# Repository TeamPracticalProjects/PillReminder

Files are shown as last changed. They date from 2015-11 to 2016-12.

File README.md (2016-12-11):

# PillReminder
##A collaborative project by [Team Practical Projects](https://github.com/TeamPracticalProjects)

##What is the Pill Reminder?

As a person ages, we all know, it becomes more difficult to remember to take your pills. At some point a person is capable of living independently, but may not remember the current day of the week, or even what time of day. This can lead to a person taking more pills than they should, or to skipping a set of pills. The Pill Reminder is meant to be used by a person in this situation.

The assembled Pill Reminder project has 14 pill cups; one for AM and one for PM, all seven days of the week. Each pill cup has an LED associated with it. The LEDs are controlled by an Arduino processor. Only one LED is ever lit at a time. The Arduino keeps track of date and time so that the correct LED is on between 6am and noon, and another between 6pm and midnight. Our hope is that the user can be easily trained to only take pills when one of the LEDs is lit up. The LED that is on will tell them which pill cup to empty; if that cup is already empty, then they should not take more pills.

The care giver is responsible for assuring the correct operation of the Pill Reminder and for loading the pill cups as appropriate.

##How do you buy a Pill Reminder?

You can't buy one. The Pill Reminder is a do-it-yourself project. All the information you need to buy the parts and assemble you own Pill Reminder can be downloaded from this site - and it's free for non-commercial use!

##The History

The Pill Reminder is a project that came about through a conversation at a Baby Boomer Makers meet-up held at the Mid Peninsula TechShop (www.techshop.ws) one cold winter evening in 2013. Bob Glicksman had the idea for the Pill Reminder and said he always wanted to make one, but he could not find the right case. Jim Schrempp had been looking for a project and said, “if you make two of the electronics I'll make two of the cases.” That night the collaboration was born.

Bob and Jim agreed to make the project and release the plans as an open source project freely licensed for non-commercial use. As a user of these open source plans you make make one, or several, for you own use but you cannot make them to sell. If you modify the plans or kits in some way you are obligated to publish your modifications and to also license your modified plans under the same terms. Your modified plans must contain attribution back to Bob Glicksman and Jim Schrempp.

Since we built this project, there have been a number of sophisticated smart phone apps released to help with medication compliance. They are not suitable for someone who doesn't actively use a smart phone. Some of them have surprisingly good features. Jim did some research and wrote an article on the criteria he used and ends with a recommendation of [the best pill reminder app](https://www.techenhancedlife.com/citizen-research/best-pill-reminder-app-explorer-choice).

We hope you enjoy the project!  
Jim Schrempp and Bob Glicksman  
San Francisco Bay Area  
February 2014

Here's a [video of an early version](https://www.youtube.com/watch?v=8NOZzQJS1Nk) of the Pill Reminder.

Tags: pill reminder, drug reminder, prescription reminder, free, open source

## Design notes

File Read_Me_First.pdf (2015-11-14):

Pill Reminder – release 1.0

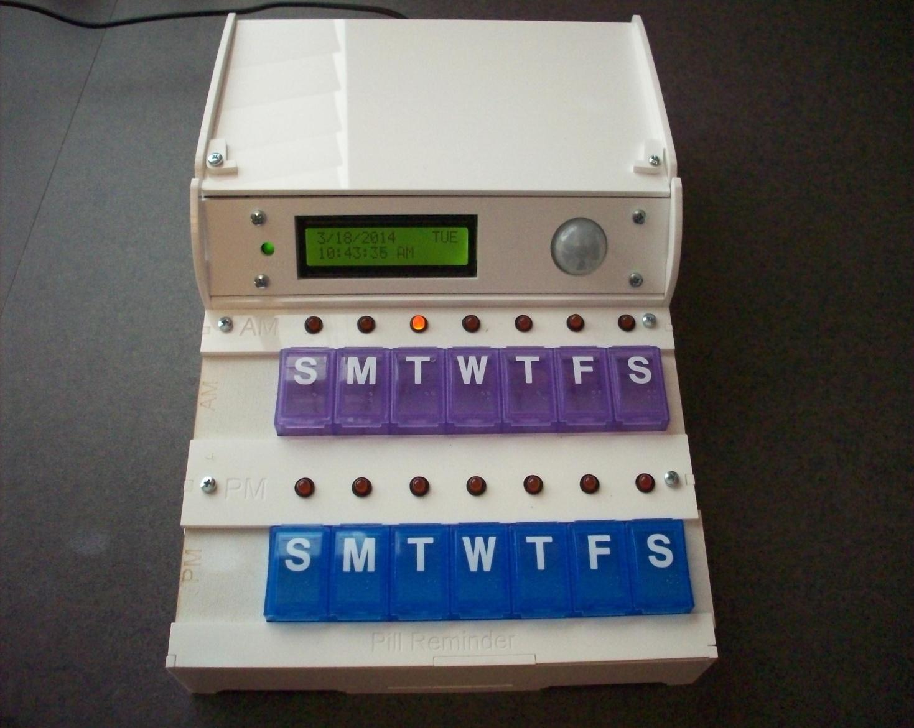
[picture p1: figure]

© 2014 Shrimpware LLC. All rights reserved.

# Pill Reminder

# Introduction and Overview of the version 1.0 Release Package

### Shrimpware LLC

5/14/2014

### Read this document first!

© 2014 Shrimpware LLC | Page 2

## License and Disclaimer

The Pill Reminder is subject to the terms of use, licenses and disclaimers contained in the document “Terms_Of_Use_License_and_Disclaimer” that is included with this release package. This document can also be viewed at: http://www.shrimpware.com/pillreminder/TOU.html

Copyright © 2014 Shrimpware LLC. All rights reserved.

The material contained within this release package may not be copied, duplicated, or reproduced in whole or in part using any method, for any reason, or under any circumstances without expressed written permission by Shrimpware LLC. Individuals may download and keep one unaltered copy for non-profit, personal use of the contents.

© 2014 Shrimpware LLC | Page 3

## Table of Contents

### Contents

1 | Introduction | 4
2 | Contents of the Release Package | 5
3 | Pathways | 7
3.1 | Pathway #1: Building and Using the Pill Reminder | 7
3.2 | Pathway #2: Manufacturing Your Own Enclosure Parts or Modifying the Enclosure
Design | 7

3.3 Pathway #3: Fabricating your own Shield Board or modifying the Shield Board design. 8

3.4 | Pathway #4: Modifying the Pill Reminder Software | 8
4 | History | 10
5 | Frequently Asked Questions (FAQ) | 12
5.1 | How can I buy a Pill Reminder that is already assembled and tested? I do not wish to
purchase piece parts and build one | 12

5.2 Where can I purchase a complete set of parts for the Pill Reminder, so that I do not have
to buy parts from the many vendors in the Parts List? | 12
5.3 | How do I use and maintain the Pill Reminder once I have built and tested it? | 12
5.4 | The default pill taking times do not address my needs. How can I change these? ....... 12
5.5 | The timekeeping function of the Pill Reminder is US specific. I live in a different
country that observes “summertime” whose dates and time changes differ from US daylight
savings time. How can I modify the Pill Reminder to observe my summertime rules? | 13

5.6 I like the Pill Reminder concept, but the plans in this package are for a device that supports only morning and evening pills. I need a Pill Reminder that supports three or four
pill taking periods per day. How can I obtain a Pill Reminder that meets my needs? | 14

© 2014 Shrimpware LLC | Page 4

1 Introduction.

The Pill Reminder is a very simple to use device to remind someone to take their medications (pills). This version of the Pill Reminder supports morning and evening pill sets.

The Pill Reminder is intended to provide the User with a very simple, even intuitive, means to determine what medications may be taken at any given time and day. In this regard, the Pill Reminder differs from many other devices that are intended to alert, even nag, the User to take their pills. The Pill Reminder shows the User what medications may be taken at any given time and, by exception, what medications should not be taken at that time. The difference here is subtle, but important. The Pill Reminder is intended as an aid not only to help Users avoid missing taking their pills (under medicating), but equally to help Users avoid taking duplicate sets of pill or sets of pills spaced too closely in time (over medicating).

The Pill Reminder is released by Shrimpware LLC as an open source, do it yourself (DIY) project. This release package contains complete material to allow you to procure parts, build your Pill Reminder, operate your Pill Reminder, and possibly even modify your Pill Reminder. You must assemble the Pill Reminder yourself based upon the documentation contained in this release package. Shrimpware LLC is not a manufacturer, supplier or distributor of the Pill Reminder, nor of any of its component parts, nor of the documentation in this release package. Shrimpware LLC is only acting as a repository from which you may download this release package and the documentation contained herein.

The material in this release package is subject to terms of use, license and disclaimers contained in the document “Terms_Of_Use_License_and_Disclaimer” that is included with this release package. This document can also be viewed at: http://www.shrimpware.com/pillreminder/TOU.html

You may use any material in this release package for your own personal and non-commercial use, according to the license described in the aforementioned “Terms_Of_Use_License_and_Disclaimer” document.

The material in this release package requires that you build the Pill Reminder yourself, using only the materials and documentation contained herein. Please review all materials and documents in this package prior to purchasing any parts or attempting any assembly. It is your responsibility to ensure that you have the skills, tools and means to complete and use the Pill Reminder safely, using only the materials contained herein. Shrimpware LLC cannot provide technical support and you are on your own if you run into problems or have trouble completing the Pill Reminder or making it work.

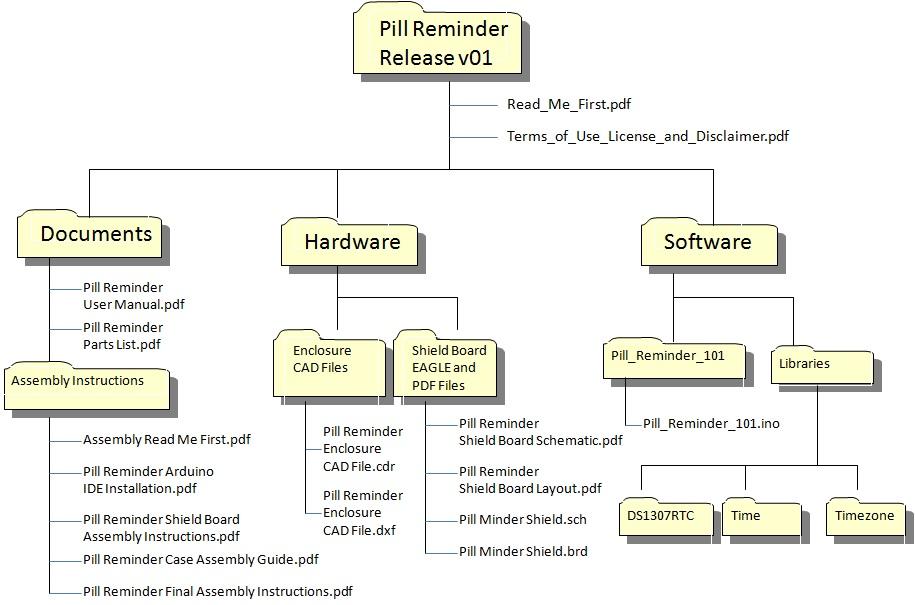
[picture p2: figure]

© 2014 Shrimpware LLC | Page 5

2 Contents of the Release Package.

The diagram below depicts the contents and organization of this release package. The release package is a .zip archive and you must download this archive to your computer and unzip it before you can access any of the material contained herein.

This release package is organized as a series of folders and subfolders, as shown in the figure above. A brief description of the package contents, by folder, is given below:

- Top Level Folder. The top level folder “Pill Reminder Release v01” contains this document and the document “Terms_Of_Use_License_and_Disclaimer”. You must read and agree to all of the terms and conditions in the latter document before you have permission to use any other material in this package.
- Documents. The “Documents” folder contains all of the documents that you will need to build and to operate the Pill Reminder. The folder contains the User Manual and Parts List. The subfolder “Assembly Instructions” contains a series of documents for assembling and testing the major subsystems of the Pill Reminder, as well as Final Assembly Instructions for integrating and testing the Pill Reminder. The document “Assembly Read Me First” will lead you though the rest of the documents in this subfolder.

© 2014 Shrimpware LLC | Page 6
- Hardware. This folder contains CAD files for both the enclosure and the shield board. You do not need these files to build and operate the Pill Reminder. They are provided as part of the open source concept so that you have complete information about the Pill Reminder, including files that you can use, subject to the open source license, to make your own modifications to the Pill Reminder.
- Software. This folder contains the software files that you must compile and upload to your Pill Reminder in order for it to operate. The Pill Reminder software, in the folder “Pill_Reminder_101” is source code that you can alter, subject to the open source license, to make your own modifications to the Pill Reminder. This software is written in the “wiring” language for the Arduino computer that is part of the Pill Reminder. You do not need to make any modifications to this software to build and operate the Pill Reminder, but you do need to compile it and upload it to your Arduino Uno microcontroller board, along with the libraries contained in the “Libraries” subfolder, in order for the Pill Reminder to operate. Complete instructions for installing the Arduino IDE on your computer, for adding the libraries in this package to your IDE, and for compiling and uploading the software to the Arduino Uno board that is part of the Pill Reminder, are contained in the document “Pill Reminder Arduino IDE Installation” that is included in
the “Documents | Assembly Instructions” folder.

© 2014 Shrimpware LLC | Page 7

3 Pathways.

The documentation that is included in this release package and described in section 2 above may be used in a number of application pathways. The pathways and the documents needed for each are described in this section.

3.1 Pathway #1: Building and Using the Pill Reminder.

The “Documents” folder contains all of the instructions that you need to build and operate the Pill Reminder. Under “Documents” you will find the User Manual and the Parts List. The Parts List contains a list of all parts (but not tools and materials) that you will need to buy in order to assemble one or more Pill Reminders. All parts can be ordered over the Internet using the links provided in the Parts List. It must be noted that certain links in the Parts List provide more parts than are needed for a single Pill Reminder; i.e. 3 shield boards (one is needed), 20 micro pushbutton switches (3 are needed), etc. This is an inevitable consequence of a small quantity build and you might want to find other Pill Reminder builders to consolidate a parts order for more cost effective parts procurement.

The “Assembly Instructions” subfolder contains a series of documents that describe, in annotated step by step detail, the assembly instructions for all parts of the Pill Reminder, and for the integration and testing of these parts into a finished unit. The “Assembly Read Me First” document provides a detailed overview. Each of the detailed assembly documents lists the tools and materials needed for that stage of the assembly.

You should read through all documents in the “Documents” folder first, before you order any parts, begin any assembly, or otherwise undertake any part of this project. It is your responsibility to ensure that you are prepared to undertake a project of this scope and magnitude.

### 3.2 Pathway #2: Manufacturing Your Own Enclosure Parts or Modifying the Enclosure

Design.

The folder “Hardware | Enclosure CAD Files” contains two versions of the 2D CAD drawings
for the parts needed to build the Pill Reminder enclosure. You do not need to use these files because the Parts List contains a link to a vendor that can supply these parts, pre-cut, for you. However, you may elect to fabricate these parts yourself, for which you will need these CAD files and a laser cutter.

There are two CAD files in this subfolder. The files are for the identical design and you only need one of them. The file “Pill Minder.cdr” is in Corel Draw’s internal file format, and the file “Pill Minder.dxf” is the same CAD file converted to this more common format. These CAD files are provided to you as-is. We have made our best effort to ensure accuracy and correctness of the data therein; however, if you use them, you are on your own!

© 2014 Shrimpware LLC | Page 8

You may also use these files to modify the enclosure in Coral Draw or using any other 2D CAD program that you can import either of these files into. Any modifications that you make are subject to the terms and conditions, license and disclaimers contained in the document “Terms_Of_Use_License_and_Disclaimer” that is included with this release package.

### 3.3 Pathway #3: Fabricating your own Shield Board or modifying the Shield Board

design.

The folder “Hardware | Shield Board EAGLE and PDF Files” contains the following
information:
- “Pill Reminder Shield Board Schematic.pdf” is a pdf version of the shield board schematic diagram. It is provided for those who wish to view, but not modify, the schematic.
- “Pill Reminder Shield Board Layout.pdf” is, likewise, a pdf version of the shield board printed circuit layout. It is provided for those who wish to view, but not modify, the board layout.
- The files “Pill Minder Shield.sch” and “Pill Minder Shield.brd” are EAGLE files produced by the EAGLE electronic CAD software from Cadsoft corporation (version 6.5.0). See www.cadsoft.de for further information or to download a free, hobbyist version of this software.

You do not need any of these files to build or use the Pill Reminder, as the blank shield board can be procured from a vendor listed on the Parts List. However, you may use the EAGLE CAD files to procure shield board PC boards from another vendor of your choice, to manufacture your own shield boards if you have printed circuit manufacturing capability, or to modify the shield board electronic design to tailor the Pill Reminder to your needs. Any modifications that you make are subject to the terms and conditions, license and disclaimers contained in the document “Terms_Of_Use_License_and_Disclaimer” that is included with this release package.

3.4 Pathway #4: Modifying the Pill Reminder Software.

The folder “Software | Pill_Reminder_101” contains the source code for the Pill Reminder. It is
provided to you subject to the terms and conditions, license and disclaimers contained in the document “Terms_Of_Use_License_and_Disclaimer” that is included with this release package.

The software is written in the “wiring” language, which is the standard programming language for the Arduino. The software has been written, compiled and tested under the Arduino IDE version 1.0.5. You do not have to make any modifications to this software, nor know anything about the wiring language or programming an Arduino, in order to build the Pill Reminder and use it as described in the User Manual. However, we have attempted to extensively comment the

© 2014 Shrimpware LLC | Page 9

source code so that you can understand it, if you wish, and make modifications to it as you see fit. Any modifications that you make to the Pill Reminder software is your own responsibility and Shrimpware LLC cannot provide and consultation or technical support regarding the released software or any modification(s) that you make therein.

See section 5, FAQ, for a discussion of some specific changes that you might wish to make in the Pill Reminder software in order to further customize it to meet some specific needs.

© 2014 Shrimpware LLC | Page 10

4 History.

The Pill Reminder is a project that came about through a conversation at a “Baby Boomer Makers, Hackers, and Entrepreneurs” meet-up held at the Mid Peninsula TechShop (www.techshop.ws) one cold January evening in 2014. Bob Glicksman had the idea for the Pill Reminder and said he had wanted to make one for a long time, but he could not find the right case. Jim Schrempp had been looking for a project and said: “if you design the electronics, I will design the enclosure.” That night, the collaboration was born.

Bob was inspired to invent the Pill Reminder out of need to support his elderly mother (“Mom”). Mom has dementia and near total short term memory loss. Bob had long supplied her with her medications in weekly “AM/PM” pill organizers. Bob would call Mom twice a day, morning and evening, to remind her to take her medications. Nevertheless, at the weekly refill time, Bob would frequently find either that Mom had missed taking some pills, or alternatively (perhaps worse), Mom would call a day or two before the pills should have run out to say that she was out of pills (meaning that she took multiple day doses, possibly leading to overdosing).

Bob experimented with many products and means to help Mom prevent overdosing; for example, mounting a clock over bathroom sink with the day of the week displayed in large letters. Nevertheless, the compliance issues persisted. Bob came up with the basic Pill Reminder concept after being frustrated with failure after failure of existing products to solve the problem. Bob reasoned that the issue with Mom was a failure to comprehend when to take what medicines and when not to take some medicines. Bob thought that a simple and intuitive method of signaling Mom when she could open a pill dispenser slot (and take any pills therein), and when she should not open a slot, would be the key to solving the problem.

The “Baby Boomer Makers, Hackers, and Entrepreneurs” meet-up group was of great assistance in flushing out the device requirements, present and potential future features, and in finalizing a development specification. Jim and Bob then went off to design, develop, test and document the Pill Reminder.

As of the date of this writing, Mom has had her Pill Reminder for over 4 weeks and has achieved 100% compliance throughout. Previously, Mom would have a fully compliant week only once in every three, on the average. Four weeks in a row of perfect compliance is highly significant, even given that it is early in deployment and testing.

The only instructions given to Mom were: “if a light is lit, open the dispenser slot under the light and take any pills in it. If there are no pills in it, then you have already taken them, even if you don’t remember doing so. Under no circumstances are you to open a dispenser slot when the light above it is not lit”. In follow up research, Mom has been unable to articulate the meaning of the light over each pill slot. Clearly, then, these excellent early results demonstrate that Pill Reminder operation is quite intuitive (a major goal when dealing with people with short term memory loss).

To date, Bob and Jim have constructed three additional Pill Reminders from the plans and instructions released in this package. Although these three devices have not yet been deployed to people who really need them, they are all running and proving (a) that the build instructions

© 2014 Shrimpware LLC | Page 11

seem to be clear and complete, and (b) that the Pill Reminders operate reliably in a “real world” environment.

Bob and Jim agreed early on to release the Pill Reminder plans as an open source, do it yourself (DIY) project, freely licensed for non-commercial use. By including all source code and source CAD files, they hope that people will not only make Pill Reminders for their own use or as gifts, but will customize and modify the design and openly and freely share their efforts with the user community. For example, you can use the 2D mechanical CAD files to make your own enclosure. The enclosure can be cut from 3mm Baltic birch plywood for “cheap but cheerful” version, and spray painted however you like. Alternatively, the pieces can be cut out of your favorite color 3mm (0.118 inch) acrylic for the more “real product” look. If you are so inclined, you might want to use a 2D CAD program to modify the design of the enclosure to create a different look, or to better fit onto a bathroom sink or night stand. We would be very interested in other people’s ideas for improvement. Please e-mail your thoughts, ideas, experiences, and modifications to pillreminder@shrimpware.com.

© 2014 Shrimpware LLC | Page 12

5 Frequently Asked Questions (FAQ).

This section contains some frequently asked questions and their answers.

### 5.1 How can I buy a Pill Reminder that is already assembled and tested? I do not wish to

purchase piece parts and build one.

As of this writing, the Pill Reminder is only available as an open source, do it yourself (DIY) project, based upon the material in this release package. Nobody is presently licensed to manufacture or sell fully or partially assembled Pill Reminders. If you are interested in manufacturing or selling fully or partially assembled Pill Reminders, please contact us at: pillreminder@shrimpware.com

### 5.2 Where can I purchase a complete set of parts for the Pill Reminder, so that I do not

have to buy parts from the many vendors in the Parts List?

As of this writing, the Pill Reminder is only available as an open source, do it yourself (DIY) project, based upon the material in this release package. Nobody is presently licensed to manufacture or sell parts kits or partially assembled Pill Reminders. If you are interested in manufacturing or selling parts kits or partially assembled Pill Reminders, please contact us at: pillreminder@shrimpware.com

### 5.3 How do I use and maintain the Pill Reminder once I have built and tested it?

Please see the User Manual for complete information about operating and maintaining your Pill Reminder. The “Pill Reminder User Manual” can be found in the “Documents” folder of this release package.

### 5.4 The default pill taking times do not address my needs. How can I change these?

The Pill Reminder software uses generic times for allowable taking of AM and PM pills. These times are specified by defined constants in the Pill Reminder software. Since you have the source code available, you may change these defined constants to fit your needs.

When you open the Pill Reminder software in the Arduino IDE, you can read more about these defined constants in the comments at the top of the program (lines 11 through 20). You can change the defined constants that control these times by editing lines 159 through 162 of the software. You must then recompile and upload the software to your Pill Reminder (Arduino Uno board) in order for the new times to take effect.

Please note that the software design requires that you leave at least one minute between AM off time and PM on time, and likewise between PM off time and AM on time. If you do not do so, the proximity sensor will not re-arm and the LEDs will not blink when the proximity sensor is tripped the first time during any pill taking period.

© 2014 Shrimpware LLC | Page 13

You are fully responsible for any and all changes that you make to the Pill Reminder software. If you do make changes to the software, please make sure to test your revised software completely and thoroughly before releasing the altered Pill Reminder for use. Please note that you are required, under our licensing agreement, to release your modifications as open source, non-commercial and provide proper attribution to us.

### 5.5 The timekeeping function of the Pill Reminder is US specific. I live in a different

country that observes “summertime” whose dates and time changes differ from US daylight savings time. How can I modify the Pill Reminder to observe my summertime rules?

The Pill Reminder software uses a “Timezone” library written by Jack Christensen and downloaded from https://github.com/JChristensen/Timezone.

Lines 187 and 188 of the Pill Reminder software define structures that are used by this library to implement changes from standard time to daylight savings time and again from daylight savings time back to standard time. The two lines of code are:

- TimeChangeRule dt = {"DT", Second, Sun, Mar, 2, 60};
- TimeChangeRule st = {"ST", First, Sun, Nov, 2, 0};

You can read about these structures, and how to change them, in the documentation for the Timezone library at the url given above. Specifically, the second and third arguments specify which day of which month (4th argument) the change is to take place, and the last argument specifies the magnitude of the change in minutes. Consequently, the change “DT” (first argument) is to take effect beginning on the Second, Sunday (Sun), at 2 AM, and it is to add 60 minutes to the “normal” time. Likewise, the change “ST” (first argument) is to take effect beginning on the First, Sunday (Sun), at 2 AM, and it is to add zero minutes to the “normal” time.

Please note that the Pill Reminder software does not use the Timezone library to convert to and from UTC, as the library’s author intends. It only uses the Timezone library to implement a one hour (60 minute) shift from the standard to daylight savings time, according to the dates and times defined in these structures.

Since you have the Pill Reminder source code, you can open it in the Arduino IDE and make any changes that you wish. You can change these structures to change the dates and time of day that the changes to and from summertime take place in your locale, as well as the magnitude of the change (in minutes). You must then recompile and upload the software to your Pill Reminder (Arduino Uno board) in order for the new daylight savings time definitions to take effect.

© 2014 Shrimpware LLC | Page 14

You are fully responsible for any and all changes that you make to the Pill Reminder software. If you do make changes to the software, please make sure to test your revised software completely and thoroughly before releasing the altered Pill Reminder for use. Please note that you are required, under our licensing agreement, to release your modifications as open source, non-commercial and provide proper attribution to us.

### 5.6 I like the Pill Reminder concept, but the plans in this package are for a device that

supports only morning and evening pills. I need a Pill Reminder that supports three or four pill taking periods per day. How can I obtain a Pill Reminder that meets my needs?

This release of the Pill Reminder only supports AM and PM pills. Extensive changes would need to be made in order to support more pill taking times. These changes include:

- Re-design of the enclosure to hold more pill dispensers and house more LEDs.
- Re-design of the shield board to extend the shift register that drives the LEDs and to add connectors for the extra LEDs.
- Extensive changes to the software in order to accommodate more LEDs and act upon more pill taking intervals.

This release package contains all of the source files (mechanical CAD, electrical CAD, and software source) for the Pill Reminder and it is therefore possible to use this material to re-design the Pill Reminder for more pill taking times. The scope of this effort is large, however, and you should only attempt it if you have the necessary skills in mechanical design, electrical design and Arduino software development that are all needed to make such an extensive re-design work. If you do accomplish this, please follow the license requirements and release your modifications as open source, non-commercial, with proper attribution to us. And please let us know that you did this by e-mailing to: pillreminder@shrimpware.com

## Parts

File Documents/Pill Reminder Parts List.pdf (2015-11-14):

Shrimpware LLC | PILL REMINDER | Parts List
Assembly | Item | Qty | Part Number | Source | Description | On-Line Purchase Link | Unit Price | Ext Price | Notes
Enclosure
Parts kit | 1 | 1 | N/A | Make it yourself or order from Prawn Designs | Kit of parts for assembling the enclosure | http://www.prawndesigns.com | | $30.00 | The enclosure parts can be fabricated using the CAD files an Assembly instructions in this release package.
; info@prawndesigns.com
Pill Dispenser | 2 | 4 | Weekly Pill Planner with Snap-Tight Lids, CVS p/n
| | | 715123
CVS Pharmacy | Removable plastic weeekly pill
dispenser

http://www.cvs.com/shop/product-detail/CVS-Large-Weekly-Pill-Planner?skuId=715123 (http://www.cvs.com/shop/product-detail/CVS-Large-Weekly-Pill-Planner?skuId=715123)

$2.99 | $11.96 | Best to get two colors, e.g. 2 ea
clear for AM and 2 ea Blue for PM
LED - yellow | 3 | 7 | LED panel mount, amber; PN 607-5102H3-5V
Mouser | Panel mount amber LED with
internal resistor and 6" pigtail leads ("AM" day indicators)

http://www.mouser.com/ProductDetail/Chicago-Miniature/5102H3- (http://www.mouser.com/ProductDetail/Chicago-Miniature/5102H3-5V/)

$1.30 | $9.10 | LED with internal resisotor; Amber
for AM LEDs
LED- green | 4 | 8 | LED panel mount, green; PN 607-5102H5-5V
Mouser | Panel mount green LED with
internal resistor and 6" pigtail leads ("PM" day indicators and power on http://www.mouser.com/Prod (http://www.mouser.com/ProductDetail/Chicago-Miniature/5102H3-5V/) uctDetail/Chicago-Miniature/5102H5- (http://www.mouser.com/ProductDetail/Chicago-Miniature/5102H5-5V/)
$1.30 | $10.40 | LED with internal resisotor; Green
for PM and Power LEDs
Display | 5 | 1 | LCD display, 16x2, backlit; ID: 181
Adafruit | 16x2 character LCD display, backlit,
HD44780 controller

http://www.adafruit.com/prod (http://www.mouser.com/ProductDetail/Chicago-Miniature/5102H5-5V/) ucts/181 (http://www.adafruit.com/products/181)

$9.95 | $9.95 | Can get two for 4.98 here:
http://www.ebay.com/itm/2pcs-1602-16x2-Character-LCD-Display-Module-HD44780-Controller-yellowblacklight-
/400446382818?ssPageName=ADM E:X:RTQ:US:1123
Proximity Sensor | 6 | 1 | 5V PIR module, 3.3V output; ID: 189
Adafruit | Passive infra-red proximity sensor,
with 3 pin cable

http://www.adafruit.com/products/189 (http://www.adafruit.com/products/189)

$9.95 | $9.95
Real-time clock | 7 | 1 | High accuracy "Chronodot" RTC I2C Module; ID: 255
Adafruit | Real-time, battery backed, clock
module, DS3231 based, I2C
interface

http://www.adafruit.com/products/255 (http://www.adafruit.com/products/255)

$17.50 | $17.50 | Compatible for DS1702 based RTC
modules, but this model uses temp[erature compensated internal crystal for high accuracy and stability.
Microcontroller | 8 | 1 | Arduino Uno R3 board; Mouser P/N 782-A000066
Mouser | Arduino Uno Rev 3 microcontroller
board.

http://www.mouser.com/ProductDetail/Arduino/A000066/?qs=sGAEpiMZZMtE4ePzUE8d2Ju
FIVM5Ac0l (http://www.mouser.com/ProductDetail/Arduino/A000066/?qs=sGAEpiMZZMtE4ePzUE8d2JuFIVM5Ac0l)
$24.51 | $24.51 | Also available from Adafruit:
http://www.adafruit.com/products/50
Cable, separable | 9 | 1 | 40 wire, female pin header cable, separable; ID: 266
Adafruit | Separable 0.1" pin header female-
female cables.

http://www.adafruit.com/products/266 (http://www.adafruit.com/products/266)

$6.95 | $6.95 | Many alternate sources available.
Power Adaptor | 10 | 1 | 9 volt DC wall wart power supply; Mean Well P/N GS06U-2P1J
Jameco | 9 volt, 660 ma, DC "wall wart"
power adapter, for Arduino http://www.jameco.com/webapp/wcs/stores/servlet/Product_10001_10001_1940686_-1 (http://www.jameco.com/webapp/wcs/stores/servlet/Product_10001_10001_1940686_-1)
$9.49 | $9.49
USB Cable | 11 | 1 | USB A/B cable; ID: 62 | Adafruit | USB cable for programming the Arduino Uno

http://www.adafruit.com/products/62 (http://www.adafruit.com/products/62)

$4.00 | $4.00
Pin header | 12 | 1 | 10 pcs 1x36 breakable male pin header; ID: 392 | Adafruit | Breakable, male, PB board solderable, 0.1" pin headers

http://www.adafruit.com/products/392 (http://www.adafruit.com/products/392)

$4.95 | $4.95
Mounting Hardware | 13 | 14 | metal screw, 4 - 40; p/n 534-9901
Mouser | Flat head 4 - 40 metal screw, 3/8"
long

http://www.mouser.com/ProductDetail/Keystone-Electronics/9901/?qs=sGAEpi MZZMtFmYSM%2fWUJwjMM2
jkmYE8TyGoG3vEKdJ8%3d (http://www.mouser.com/ProductDetail/Keystone-Electronics/9901/)
$0.10 | $1.40
Mounting Hardware | 14 | 4 | metal standoff, 4 - 40; p/n 761-2112-440-AL-7
Mouser | Double sided, 4 - 40 metal
standoff, 1" high

http://www.mouser.com/ProductDetail/RAF-Electronic-Hardware/2112-440-AL-7/?qs=sGAEpiMZZMtrde5aJd3
qw8BUoqM2q3%252bQgGcuZ
%252bZQnXw%3d (http://www.mouser.com/ProductDetail/RAF-Electronic-Hardware/2112-440-AL-7/)
$0.40 | $1.60
pp 1 of 3 | 5/22/14 | Copyright (c) Shrimpware LLC. All rights reserved.

Mounting Hardware | 15 | 10 | metal nut, 4 - 40; p/n 534- 7235-3
Mouser | 4 - 40 metal hex nut | http://www.mouser.com/Prod
uctDetail/Keystone-Electronics/7235-
3/?qs=sGAEpiMZZMtFmYSM%
2fWUJwjMM2jkmYE8TVaKr94Y
YEsQ%3d (http://www.mouser.com/ProductDetail/Keystone-Electronics/7235-3/)
$0.06 | $0.60
Mounting Hardware | 16 | 7 | nylon screw, 4 - 40; p/n 534-9328
Mouser | flat head nylon screw, 4 - 40, 3/8"
long

http://www.mouser.com/ProductDetail/Keystone-Electronics/9328/?qs=sGAEpi MZZMtFmYSM%2fWUJwjMM2
jkmYE8TDv833dWoJEQ%3d (http://www.mouser.com/ProductDetail/Keystone-Electronics/9328/)
$0.13 | $0.91
Mounting Hardware | 17 | 2 | nylon screw, 4 - 40; p/n 534-9527
Mouser | flat head nylon screw, 4 - 40, 1/4"
long

http://www.mouser.com/ProductDetail/Keystone-Electronics/9527/?qs=sGAEpi MZZMtFmYSM%2fWUJwjMM2
jkmYE8T6M5YAr%2f3kG0%3d (http://www.mouser.com/ProductDetail/Keystone-Electronics/9527/)
$0.13 | $0.26
Mounting Hardware | 18 | 1 | nylon standoff, 4 - 40; p/n 524-1902C
Mouser | double sided, 4 - 40 nylon standoff,
1/2" long

http://www.mouser.com/ProductDetail/Keystone-Electronics/1902C/?qs=sGAEpi MZZMtrde5aJd3qw3QaZpWtG
6nidQne%2f0XWhd0%3d (http://www.mouser.com/ProductDetail/Keystone-Electronics/1902C/)
$0.63 | $0.63
Mounting Hardware | 19 | 9 | nylon nut, 4 - 40; p/n 561- G440
Mouser | 4 - 40 nylon hex nut | http://www.mouser.com/Prod
uctDetail/Eagle-Plastic-Devices/561-
G440/?qs=sGAEpiMZZMtFmYS
M%2fWUJwsXnGnuBfRdpCfiad
u46AF8%3d (http://www.mouser.com/ProductDetail/Eagle-Plastic-Devices/561-G440/)
$0.19 | $1.71
Mounting Hardware | 20 | 1 | nylon screw, 2 - 56; bag | Frys Electronics | flat head nylon screw, 2-56, 1/2" long

http://www.frys.com/product/3579354?site=sr:SEARCH:MAIN_RSLT_PG (http://www.frys.com/product/3579354?site=sr:SEARCH:MAIN_RSLT_PG)

$2.19 | $2.19
Mounting Hardware | 21 | 1 | nylon nut, 2 - 56; bag | Frys Electronics | 2-56 nylon hex nut | http://www.frys.com/product/ 3580404?site=sr:SEARCH:MAI N_RSLT_PG (http://www.frys.com/product/3580404?site=sr:SEARCH:MAIN_RSLT_PG)
$2.19 | $2.19
Crimp Connectors | 22 | 0 | Box of 100 closed end insulated crimp connectors; Ace p/n
| | | 3015534
Ace hardware | Closed end crimp connectors, #22-
#14 AWG

http://www.acehardware.com/product/index.jsp?productId=1286945 (http://www.acehardware.com/product/index.jsp?productId=1286945)

$0.00 | $0.00 | Note: optional - see Final Assembly
Instructions (soldering is an alternative to crimping)
Wire | 23 | 1 | #22 Stranded hookup wire, green; p/n 818-5
Jameco | #22 stranded hookup waire, PVC
insulation, green, 100 foot roll.

http://www.jameco.com/webapp/wcs/stores/servlet/Product_10001_10001_310852_-1 (http://www.jameco.com/webapp/wcs/stores/servlet/Product_10001_10001_310852_-1)

$9.95 | $9.95
Wire | 24 | 1 | #22 Stranded hookup wire, red; p/n 818-2
Jameco | #22 stranded hookup waire, PVC
insulation, red, 100 foot roll.

http://www.jameco.com/webapp/wcs/stores/servlet/Product_10001_10001_734303_-1 (http://www.jameco.com/webapp/wcs/stores/servlet/Product_10001_10001_734303_-1)

$10.95 $10.95

Shield Board
PC Board | 1 | 1 | Printed Circuit Board | OSH Park | printed circuit board for Pill Reminder shield | http://oshpark.com/shared_pr | $42.20 | $42.20 | Note: price is for three boards, which is the OSH Park minimum order. You will need to create a free account with OSH Park to order boards from this site.
ojects/hjjifcbz (http://oshpark.com/shared_projects/hjjifcbz)
pp 2 of 3 | 5/22/14 | Copyright (c) Shrimpware LLC. All rights reserved.

Stackable headers | 2 | 1 | Arduino Header, 6 pin; Adam Tech p/n RS1-06-G- .561-A11596
Jameco | 6 position female header - pass
through, Arduino

http://www.jameco.com/webapp/wcs/stores/servlet/Product_10001_10001_2144614_-1 (http://www.jameco.com/webapp/wcs/stores/servlet/Product_10001_10001_2144614_-1)

$0.49 | $0.49
Stackable headers | 3 | 2 | Arduino Header, 8 pin; Adam Tech p/n RS1-08-G- .561-A11596
Jameco | 8 position female header - pass
through, Arduino

http://www.jameco.com/webapp/wcs/stores/servlet/Product_10001_10001_2144631_-1 (http://www.jameco.com/webapp/wcs/stores/servlet/Product_10001_10001_2144631_-1)

$0.55 | $1.10
Stackable headers | 4 | 1 | Arduino Header, 10 pin; Adam Tech p/n RS1-10-G- .561-A11596
Jameco | 10 position female header - pass
through, Arduino

http://www.jameco.com/webapp/wcs/stores/servlet/Product_10001_10001_2177627_-1 (http://www.jameco.com/webapp/wcs/stores/servlet/Product_10001_10001_2177627_-1)

$0.65 | $0.65
5 | 2 | Package of 5, 3.5mm, 2 pin terminal block; ID: 724
Adafruit | 2 position 3.5mm PC board screw
terminal connector

http://www.adafruit.com/products/724 (http://www.adafruit.com/products/724)

$2.95 | $5.90
Push button switch | 6 | 1 | Package of 20 mini pushbutton switch; ID:
| | | 367
Adafruit | Momentary, SPST, NO push button
switch, miniature, PC mount http://www.adafruit.com/products/367 (http://www.adafruit.com/products/367)
$2.50 | $2.50
Potentiometer | 7 | 1 | Trim pot, 10K ohm: PN 3362P-1-103LF/76P103LF
Jameco | Trim pot, 10K, miniature, PC mount | http://www.jameco.com/weba
pp/wcs/stores/servlet/Product _10001_10001_182837_-1 (http://www.jameco.com/webapp/wcs/stores/servlet/Product_10001_10001_182837_-1)
$0.95 | $0.95
IC Shift Register | 8 | 1 | Package of 3 shift registers; ID: 450
Adafruit | 74HC595 latached shift reigster | http://www.adafruit.com/prod
ucts/450 (http://www.adafruit.com/products/450)
$2.75 | $2.75
DIP socket, 16 pin | 9 | 1 | 16 pin DIP socket; PN 6100-16-R
Jameco | DIP socket, 16 pin, PC solder mount | http://www.jameco.com/weba
pp/wcs/stores/servlet/Product _10001_10001_37402_-1 (http://www.jameco.com/webapp/wcs/stores/servlet/Product_10001_10001_37402_-1)
$0.75 | $0.75
Transistor | 10 | 1 | Package of 10 transistors, 2N2222A; ID: 756
Adafruit | 2N2222A, switching transistor,
TO92 package

http://www.adafruit.com/products/756 (http://www.adafruit.com/products/756)

$1.95 | $1.95
Resistor, 330 ohm | 11 | 1 | Package of 10 resistors, 330 ohm; PN CF1/4W331JRC
Jameco | Optional: 330 ohm, 1/4 watt, axial
resistor

http://www.jameco.com/webapp/wcs/stores/servlet/Product_10001_10001_690742_-1 (http://www.jameco.com/webapp/wcs/stores/servlet/Product_10001_10001_690742_-1)

$0.10 | $0.10 | Resistors are only needed where the
panel mount LEDs do not have internal resisors. The resistor positions are jumered if the resistors are not needed.
Resistor, 560 ohm | 12 | 1 | Package of 10 resistors, 560 ohm; PN CF1/4W561JRC
Jameco | 560 ohm, 1/4 watt, axial resistor | http://www.jameco.com/weba
pp/wcs/stores/servlet/Product Display?langId=-
1&storeId=10001&productId= 690806&catalogId=10001&CID =PDF141CAT (http://www.jameco.com/webapp/wcs/stores/servlet/ProductDisplay?langId=-1&storeId=10001&productId=690806&catalogId=10001&CID=PDF141CAT)
$0.10 | $0.10
Resistor, 5.6 Kohm | 13 | 1 | Package of 10, 5.6 Kohm resistor
Jameco | 5.6 Kohm, 1/4 watt, axial resistor | http://www.jameco.com/weba
pp/wcs/stores/servlet/Product _10001_10001_691041_-1 (http://www.jameco.com/webapp/wcs/stores/servlet/Product_10001_10001_691041_-1)
$0.10 | $0.10

Capacitor,
electrolytic
14 | 1 | 100 uf capacitor, radial, PN R100/25
Jameco | 100 uf electrolytic capacitor, 25
volt

http://www.jameco.com/webapp/wcs/stores/servlet/Product_10001_10001_93761_-1 (http://www.jameco.com/webapp/wcs/stores/servlet/Product_10001_10001_93761_-1)

$0.10 | $0.10
Capacitor, ceramic | 15 | 1 | Pacakge of 10, 0.1 uf capacitor
Jameco | 0.1 UF ceramic capacitor | http://www.jameco.com/weba
pp/wcs/stores/servlet/Product _10001_10001_151116_-1 (http://www.jameco.com/webapp/wcs/stores/servlet/Product_10001_10001_151116_-1)
$0.13 | $0.13

$240.92

pp 3 of 3 | 5/22/14 | Copyright (c) Shrimpware LLC. All rights reserved.

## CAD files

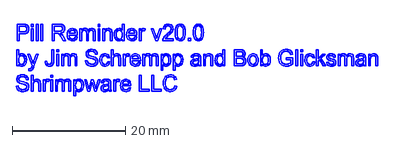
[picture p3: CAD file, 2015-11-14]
Hardware/Enclosure_CAD_Files/PillMinder.dxf
63.9 x 12.7 mm

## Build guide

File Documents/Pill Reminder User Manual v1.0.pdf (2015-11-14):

Pill Reminder – release 1.0


© 2014 Shrimpware LLC. All rights reserved.

# Pill Reminder

# User Manual

## Release 1.0

Shrimpware LLC
5/9/2014

Instructions for use and operation of the Pill Reminder.

© 2014 Shrimpware LLC | Page 2

## License and Disclaimer

The Pill Reminder is subject to the terms of use, licenses and disclaimers contained in the document “Terms_Of_Use_License_and_Disclaimer” that is included with this release package. This document can also be viewed at: http://www.shrimpware.com/pillreminder/TOU.html

Copyright © 2014 Shrimpware LLC. All rights reserved.

The material contained within this manual may not be copied, duplicated, or reproduced in whole or in part using any method, for any reason, or under any circumstances without expressed written permission by Shrimpware LLC. Individuals may download and keep one unaltered copy for non-profit, personal use of the contents.

© 2014 Shrimpware LLC | Page 3

## Table of Contents

### Contents

1 | Introduction | 4
2 | Plugging In the Pill Reminder | 7
3 | Roles and Responsibilities | 10
3.1 | User Role | 10
3.2 | Caregiver Role | 10
4 | User Instructions | 12
5 | Caregiver Instructions | 13
5.1 | Removing and Replacing the Pill Dispensers | 13
5.2 | Resetting Pill Reminder | 15
5.3 | Setting the Date and Time | 16
5.4 | Testing the Pill Reminder | 23
6 | Specifications | 24

© 2014 Shrimpware LLC | Page 4

1 Introduction.

The Pill Reminder is a very simple to use device to remind someone to take their medications (pills). This version of the Pill Reminder supports morning and evening pill sets. The Pill Reminder should be placed wherever a User usually takes their pills; generally either on a night stand or near a bathroom sink. The unit is moderately water tolerant but should not be submersed nor left wet for any period of time. The Pill Reminder must be located where it can be plugged in to AC electrical power.

The Pill Reminder’s simplicity of operation is due to 14 Light Emitting Diodes (LEDs); one above each of AM and PM pill dispenser slots for each of the 7 days of the week. The AM light for the current day of the week lights up from 6 am to noon. The PM light for the current day of the week lights up from 6 pm to midnight. The User only needs to be instructed to open the pill dispenser slot where the LED is lit and never to open any other pill dispenser slot. At any time, the User should open that slot where the LED is lit and they should take the pills therein. If there are no pills therein, the User must be trained to understand that s/he has already taken the pills, regardless of whether or not s/he remembers doing so. As such, the Pill Reminder is appropriate for people who have mild dementia, short term memory loss, or simple absentmindedness.

The Pill Reminder has a proximity sensor on the sloped front panel. The first time that the proximity sensor is tripped within an LED lit interval, the LED will blink for approximately 4 seconds. This is an added means to gain the User’s attention to taking their pills; however, the User should be trained to check the pill dispenser as often as necessary when the LED above it is lit, in order to ensure that they do not forget to take their pills.

There are no controls for the User to operate. The Pill Reminder is AC powered, but keeps time internally on battery power even when the AC power fails. The battery is good for more than 5 years of operation. The Pill Reminder automatically corrects date/time for daylight savings time (if so set) and for leap year, up to the year 2100. The internal timekeeping is accurate enough that the Pill Reminder does not need the time to be adjusted more than once per year, if that. The intent is for the Pill Reminder to be as foolproof and as simple as possible for the User: “check the dispenser slot when the LED above it is lit and take any pills therein”; period.

The Pill Reminder does not sense whether the User has opened a dispenser slot or whether the User has actually taken his/her pills. As such, it is necessary that the User have the mental capability to learn and understand the simple rules described herein. The Pill Reminder is not suitable for people with Alzheimer’s disease, severe dementia, or any other impairment which would prevent the User from understanding and executing these simple, but important, instructions.

The Pill Reminder has two removable plastic pill dispensers; one for AM pills and one for PM pills. A Caregiver must swap in filled dispensers for empty dispensers on a weekly basis. The

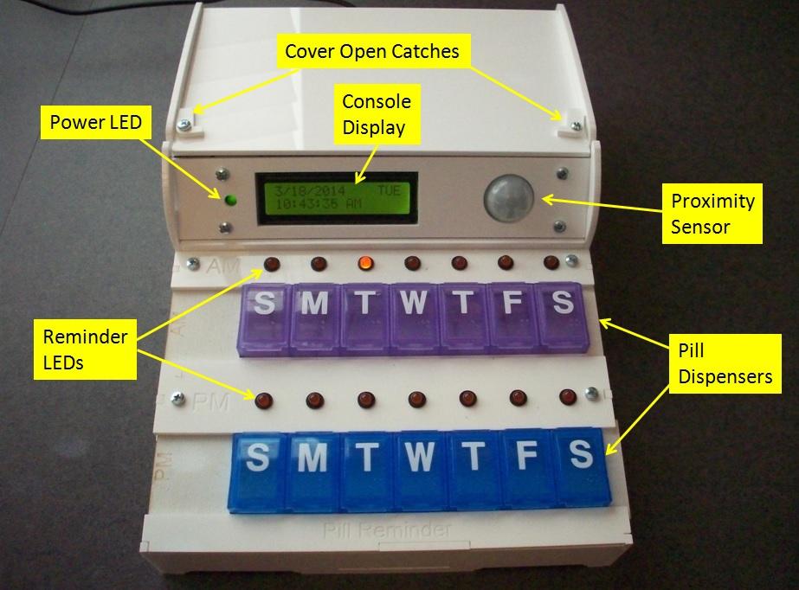
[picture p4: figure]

© 2014 Shrimpware LLC | Page 5

detailed roles and responsibilities of “User” and “Caregiver” are described further in section 2 of this document.

Figure 1-1 is an annotated picture of the Pill Dispenser. The parts of the unit, and their function, are described below.

Figure 1-1. Pill Reminder Overview.

The AM and PM pill dispensers and the LEDs associated with each pill dispenser are on the accessible front of the device. The photo in figure 1-1 shows the “Tuesday AM” LED lit, because the time (at photo taking) is 10:43 AM on a Tuesday.

The Pill Reminder has a sloping front display panel with three components:

- Power LED: This LED is lit up when external power is applied to the unit.
- Console Display: The backlit LCD display normally shows the date, day of the week, and current time. It is also used for setting the time when the unit is first installed or moved.

© 2014 Shrimpware LLC | Page 6
- Proximity Sensor: This is an infrared proximity sensor that is common on alarm systems and other applications. It will sense the presence of a person within at least 4 feet away and from an angle of at least +/- 45 degrees from center.

By design, there are no controls whatsoever that are accessible from outside of the Pill Reminder. The hinged top of the enclosure is secured in place by movable catches. The catches must be moved and the cover must be opened in order to access miniature pushbuttons to reset the unit and to set the date/time. The operation of these buttons is described in section 5 of this document.

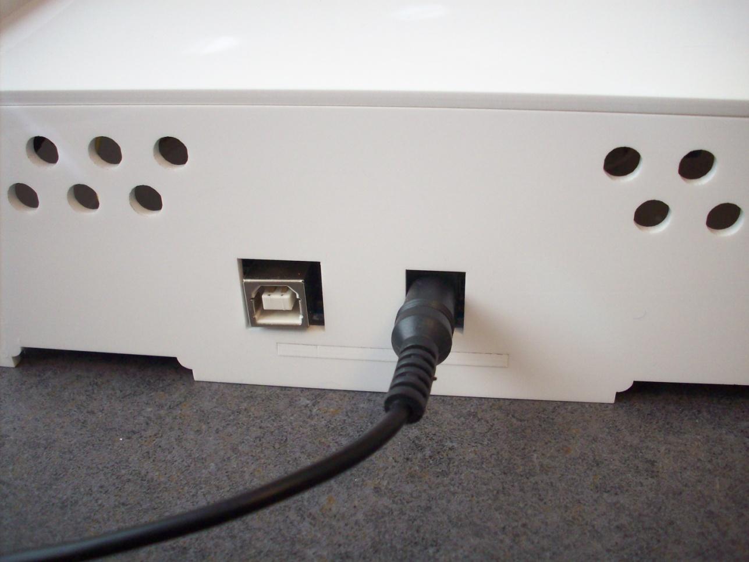
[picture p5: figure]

© 2014 Shrimpware LLC | Page 7

2 Plugging In the Pill Reminder.

The Pill Reminder is powered by AC power via a “wall wart” power supply that comes with the unit. The power supply has a 2.1 mm plug that plugs into a jack in the back of the Pill Reminder, as shown in figure 2-1.

Figure 2-1. Back of Pill Reminder, showing the power supply plugged in.

Aside from the power jack, there is a USB connector on the back of the unit. This connector is not used in normal operation. It is available for loading new software into the unit as well as for an auxiliary +5 volt power supply option. There is no power switch or other external control. The Pill Reminder is intended to be plugged in and left that way.

When the Pill Reminder is plugged in, it initially goes through a 10 second “calibration mode”. Three things happen during this time period:

- The proximity sensor calibrates itself to the room environment. In order for proper calibration, whomever plugs the unit into AC power should stand to the side or back of the unit for the 10 second calibration period, so that the proximity sensor obtains an accurate “empty room” calibration.

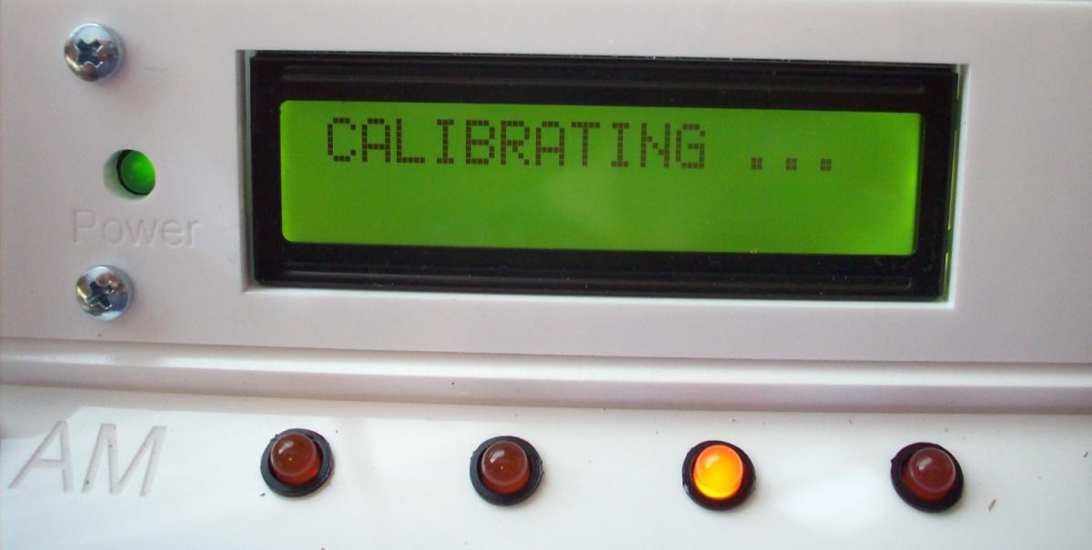
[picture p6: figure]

© 2014 Shrimpware LLC | Page 8
- The LCD display shows the messaging “CALIBRATING …”, as depicted in figure 2-2, below. At the end of the calibration period, the LCD display shows the date, day and time.

Figure 2-2. Calibration and Self test.

- The LEDs blink in succession: Sunday AM, Sunday PM, Monday AM, Monday PM, …. Saturday AM, Saturday PM, through 4 successive cycles. This is a self test to check that all of the LEDs are working properly. The person plugging the unit in should take note to ensure that all parts are working properly, as described above.

The Pill Reminder can similarly be reset via the internal “RESET” pushbutton, as described in section 5, below.

When the Calibration and Self Test period is complete:

- The proper LED (including no LED, according to the time) should light up. Note: care should be taken not to trip the proximity sensor if the person plugging in the unit (or resetting it) is not the User.
- The LCD displays the current date, current day of the week, and the current time (in 12 hour AM/PM format) on the LCD display. Note: if the time has not been previously set, or if the internal battery has been replaced, the LCD will display a message to this effect and it will be necessary to set the date/time as described in section 5 of this document.
- The proximity sensor will be armed immediately if any LED is on. It will re-arm automatically whenever the next LED comes on.

This is the normal mode of the Pill Reminder and the unit will remain in this mode as long as it is plugged in and not reset via the internal RESET pushbutton (section 5).

© 2014 Shrimpware LLC | Page 9

No further operation is necessary, unless the date/time needs to be reset (i.e. due to battery replacement or relocation of the unit to a different time zone).

© 2014 Shrimpware LLC | Page 10

3 Roles and Responsibilities.

There are two “people” roles associated with the Pill Reminder:

- User
- Caregiver

These two roles may be filled by one person or two different persons. An individual who can understand and execute all of the instructions in this document, but is “forgetful” about taking their pills can fulfill both roles. For more impaired people, the User and Caregiver roles should be assigned to separate people.

3.1 User Role.

The “User” is the person who takes the pills. The User’s responsibilities are to:

- Observe the LEDs.
- If an LED is on, open (and keep open) that pill dispenser slot directly below the lit LED.
- Take any pills in the open dispenser slot.

The User must be capable of being trained in these responsibilities, as elaborated in section 4, below. If the User is not capable of being trained in these responsibilities, then the Pill Reminder is not appropriate for them.

3.2 Caregiver Role.

The Caregiver has multiple roles and responsibilities. They are:

- Train the User thoroughly to observe the User rules stated above.
- Ensure that a fresh set of pills are properly loaded into the pill dispenser slots each and every week. The pill dispensers are removable so that the Caregiver can install a pre-filled set of dispensers once per week and take back the previous week’s empty dispensers for re-filling and replacement the following week.
- Ensure that the Pill Reminder is working correctly. This can be done by resetting the unit and observing the Calibration and Self Test cycle, as described above. The Pill Reminder can be reset in either of two ways: (1) by unplugging the power supply from the unit, waiting 5 seconds, and re-plugging the unit back in, or (2) by opening the cover and depressing the RESET pushbutton (see section 5).
- Ensure that the date and time are set correctly on the LCD display. See section 5, below, for instructions on setting the date and time.

© 2014 Shrimpware LLC | Page 11

The Pill Reminder is only an aide for helping Users to remember to take their pills. The Caregiver has overall responsibility to ensure that the User takes their medications on time, and to assess whether the User is competent to follow their training on the proper use of the Pill Reminder.

© 2014 Shrimpware LLC | Page 12

4 User Instructions.

The User instructions are, intentionally, very simple:

- If an LED is lit, open the dispenser slot under that LED and make sure that the pills in the dispenser slot are all taken.
- Check the slot where the LED above it is lit, and take any pills therein, regardless of whether the User thinks that the pills have already been taken. One way to ensure this is to train the User to keep the slot open after opening it and taking the pills, so that it remains obvious that the slot is empty.
- Never open any slot where the LED above it is not lit.

The User may also use the LCD display as a date and time clock, as it will keep time reliably, even through a power failure, and will automatically adjust for daylight savings time (if so configured) and for leap year. The LCD and LEDs will only display when AC power is on and the unit is plugged it, but the unit will keep time through a power failure and will come up with the correct date and time when power is restored.

The User may observe an error message on the LCD in the event that the internal battery needs replacement or other failure occurs. The User must be trained to inform a Caregiver immediately if the Pill Reminder is displaying an error message or otherwise not displaying the proper date and time.

The User may observe an LED blinking for about 4 seconds, and then lighting solidly. This is an added feature of the Pill Reminder that uses the proximity sensor to help catch the User’s attention when they approach the Pill Reminder for the first time during any pill taking time period. However, the proximity sensor can be triggered by other people and animals, and the User must be trained to not rely on the LED blinking to check if they have taken their pills. The User should always check the pill dispenser under a lit LED and take any pills therein immediately.

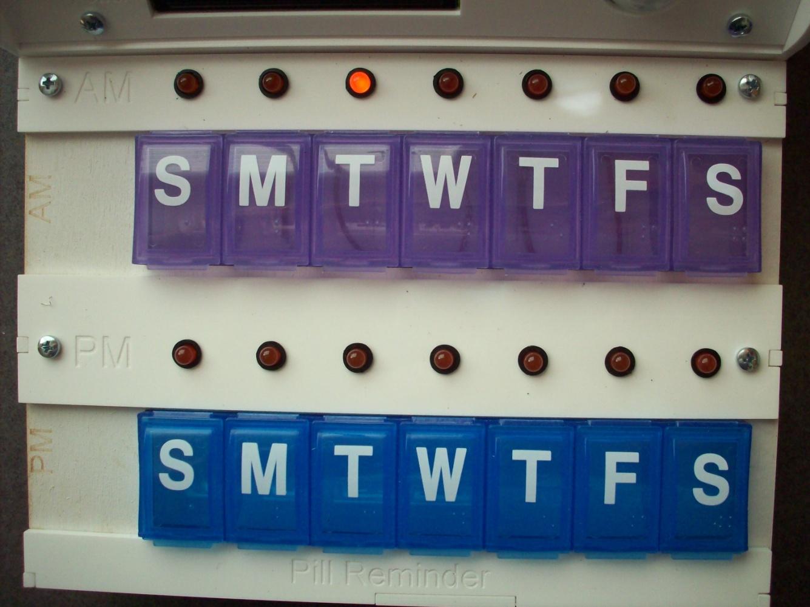
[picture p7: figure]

© 2014 Shrimpware LLC | Page 13

5 Caregiver Instructions.

5.1 Removing and Replacing the Pill Dispensers.

The Pill Reminder contains two removable 7 day pill dispensers, as indicated on figure 1-1, with a close-up in figure 5-1, below.

Figure 5-1. Pill Dispensers - Close-up

The pill dispensers are removable so that the Caregiver can replace empty ones with filled ones on a weekly basis, and take the empties away for refilling over the subsequent week. It is the Caregiver’s responsibility to ensure that the pill dispensers are refilled properly and replaced weekly, or at any time that the User requires new pills.

Figure 5-2 shows one of the two pill dispensers removed from the Pill Reminder enclosure.

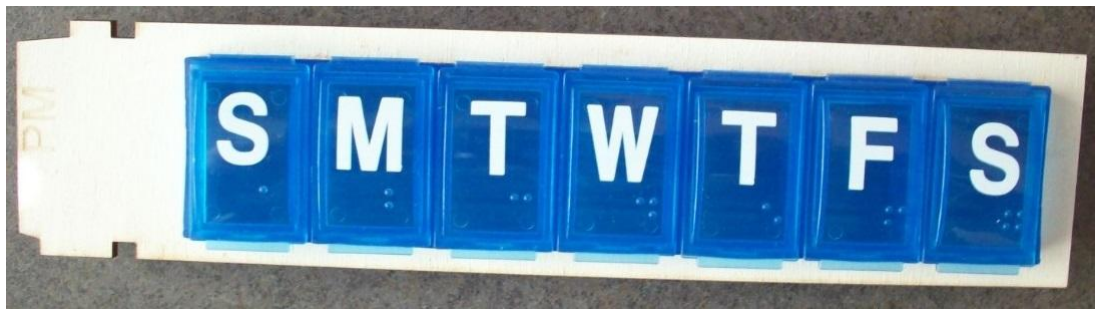
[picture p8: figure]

© 2014 Shrimpware LLC | Page 14

Figure 5-2. Removable Pill Dispenser.

Each plastic pill dispenser is pressed into a carrier that slides the pill dispenser in and out of the Pill Reminder unit. The carrier is notched on the left side to provide a positive detent to hold the pill dispenser into place at the proper location within the Pill Reminder. The pill dispenser is removed by gently, but firmly, by pulling the carrier to the right when facing the front of the Pill Reminder. The Pill Reminder enclosure is notched on the sides so that the dispenser, with carrier, will slide in and out of the enclosure without interference.

It is recommended that the Caregiver have an extra set of pill dispensers/carriers on hand. Each week, as it becomes time to refill the User’s pills, the Caregiver can bring two filled pill dispensers (one with AM pills and one with PM pills) to the User’s facility. The Caregiver should then:

- Remove the old (empty) AM and PM pill dispensers from the Pill Reminder by gently, but firmly, pulling each to the right, as viewed from the front of the unit.
- Replace the empty pill dispensers with new, refilled pill dispensers, taking care to properly place the AM and PM carriers (PM in front, AM toward the rear). Each new pill dispenser is inserted from the right side of the unit (facing forward), with the notched end to the left. The carrier is pushed into the unit, gently but firmly, until it locks into place via its detent.
- The Caregiver must double check that the correct dispenser is in the correct location, that each contains the correct pills for the correct day, that all dispenser covers are closed shut, and that the pill dispensers are fully inserted into the Pill Reminder enclosure so that each day’s dispenser slot lines up directly under the proper LED.
- The Caregiver must then take away the old, empty pill dispensers and refill them properly for replacement use the following week.

Before leaving the User’s facility, the Caregiver should check that the LCD display shows the correct day, date and time. See “Setting the Date and Time”, below, for instructions on performing this task, as necessary.

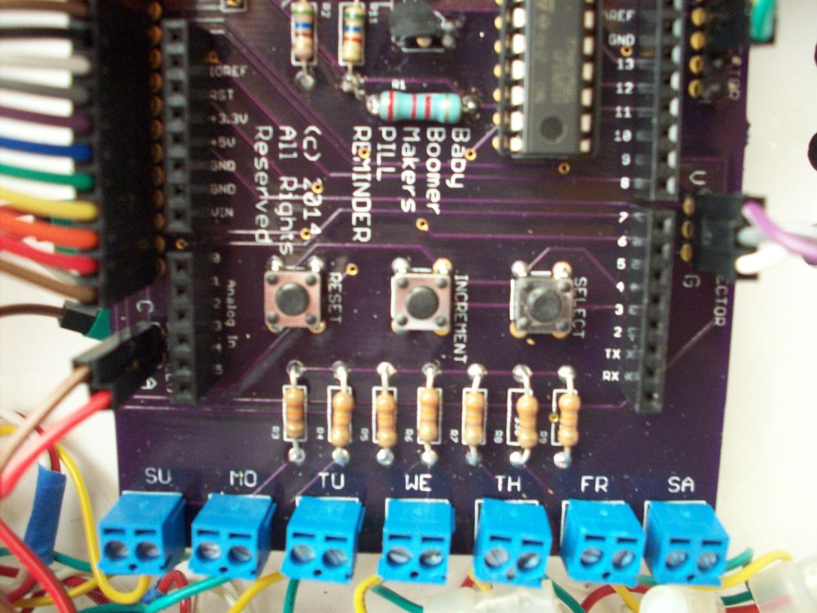
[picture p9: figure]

© 2014 Shrimpware LLC | Page 15

5.2 Resetting Pill Reminder.

Resetting the Pill Reminder is necessary in order to recalibrate and test the unit and for setting the date and time. There are two ways to reset the Pill Dispenser: via removing power and via the RESET pushbutton inside the unit.

- Removing the power: The power is removed either by unplugging the “wall wart” power supply from AC power or by removing the power plug from the rear of the Pill Reminder (figure 2-1 shows the location). Either way, the Caregiver should wait at least 5 seconds and then plug the power back in. The Pill Reminder will be reset and will enter the Calibration and Self Test mode, as described in section 2 of this document. Removing the power requires that the internal battery backup be operational in order for the unit to keep time. Otherwise, the LCD display will show a message requiring the Caregiver to set the date and time, per the instructions in section 5.3, below.
- Pressing the internal RESET button. There are three, miniature pushbutton switches inside of the Pill Reminder. In order to access these switches, the Pill Reminder’s cover open latches must be moved into the unlatched position and the top cover lifted open (refer to figure 1-1 for the detailed location). Once the top of the unit is open, a circuit board containing the three pushbuttons is accessible; see figure 5-3.

Figure 5-3. Pushbutton Switches.

© 2014 Shrimpware LLC | Page 16

Once the cover is open, the Caregiver may reset the Pill Reminder by pressing the RESET pushbutton switch (leftmost pushbutton). Resetting the unit in this manner has exactly the same effect as unplugging the power, except that the unit always remains powered and the previous time setting should be maintained regardless of the state of the internal backup battery.

Note that the Caregiver should be sure to replace the top cover and re-engage the cover open latches so that the User does not have inadvertent access to the pushbutton switches.

After resetting the Pill Reminder, the Caregiver should observe the self test to ensure that all of the LEDs are working properly and should never leave the unit without ensuring that the date, day and time are displayed properly on the LCD display after the Calibration and Self Test period is finished (approximately 10 seconds). Please refer to section 2 for details.

5.3 Setting the Date and Time.

The battery backed clock in the Pill Reminder is highly accurate and the battery should last more than 5 years. The Pill Reminder can automatically adjust for daylight savings time and for leap year; therefore, the date and time should need to be set only very infrequently. When it is necessary to change the date-time, the Caregiver is responsible to do so.

The Pill Reminder requires good timekeeping to ensure that the User takes the correct pills at the correct days and times. The Pill Reminder has therefore been designed to prevent inadvertent changing of the date-time, in two ways:

- Access to the pushbuttons for setting date and time requires the latched cover of the Pill Reminder to be opened.
- The Pill Reminder’s date-time can only be changed immediately after the unit is reset. Date-time setting can only be initiated during the 10 second Calibration and Self Test interval immediately following a device reset. One date-time changing is initiated, the Caregiver can take as long as necessary to set the date and time. Once the date and time is set, any remaining Calibration and Self Test time will be executed before the Pill Reminder enters normal operation. Once the Pill Reminder is in normal operation, it must be reset to change the date-time. Resetting the Pill Reminder is described in section 5.2, above.

In order the set the date and time, The Pill Reminder cover must be opened so that the three pushbuttons may be accessed, as described in section 5.2, above. The Pill Reminder must first be reset, as also described in section 5.2. Once the Pill Reminder is reset, it enters the Calibration and Self Test mode, as described in section 2 of this document. At anytime during the Calibration and Self Test sequence, pressing the SELECT pushbutton (rightmost, in figure 5-3), suspends Calibration and Self Test and enters time setting mode. In time setting mode, the SELECT pushbutton advances the item to be set to the next item on the list and the

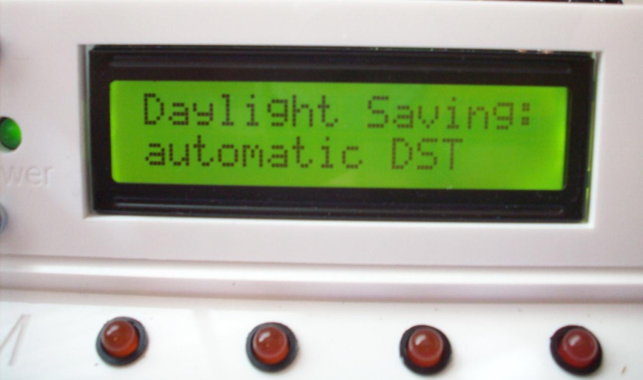
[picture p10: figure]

© 2014 Shrimpware LLC | Page 17

INCREMENT pushbutton (middle, in figure 5-3) increments that function to the next sequential value. The Caregiver may use SELECT to cycle through the functions as many times as desired. The Caregiver may also press RESET at any time to reset the date-time to the previously stored values. The date and time values set by the Caregiver are only stored into the Pill Reminder when the Caregiver presses INCREMENT at the appropriate prompt, as described below.

The following is the list of date and time setting functions that are displayed, in order, with each depression of the SELECT pushbutton. The function and its present value are displayed on the LCD:

- Daylight Saving: Immediately upon pressing SELECT during a device reset, the LCD displays “Daylight Saving:” on the first line and the selection value on the second line. The default value for the selection is “automatic DST”, as shown in figure 5-4:

Figure 5-4: Daylight Saving.

Automatic DST applies US daylight savings time rules to the current time throughout the year. Pressing INCREMENT changes the second line to “no DST”, and pressing INCREMENT again changes it back to “automatic DST”. The Caregiver uses INCREMENT to make the proper selection for the User’s locale (whether or not daylight savings time is observed there), and then presses SELECT to advance to “Year:”

- Year: When “Year:” is displayed on the first line of the LCD, the year is shown on the second line. The default year is “2014”, as shown in figure 5-5.

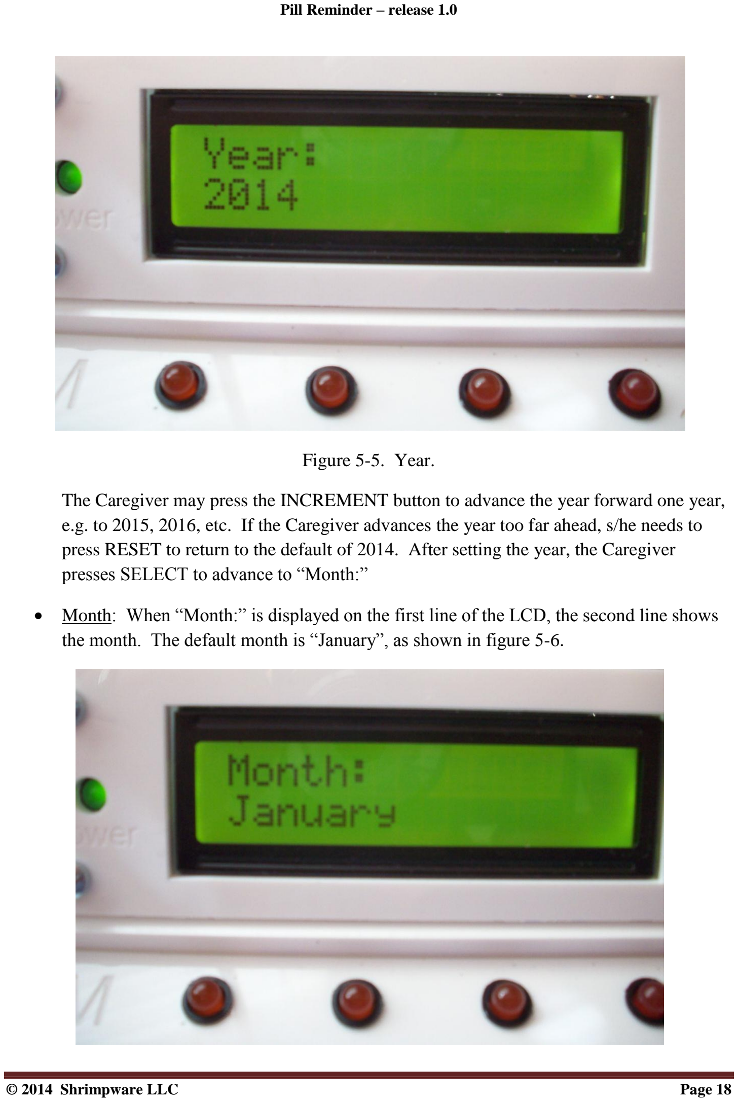
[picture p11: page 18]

© 2014 Shrimpware LLC | Page 18

Figure 5-5. Year.

The Caregiver may press the INCREMENT button to advance the year forward one year, e.g. to 2015, 2016, etc. If the Caregiver advances the year too far ahead, s/he needs to press RESET to return to the default of 2014. After setting the year, the Caregiver presses SELECT to advance to “Month:”

- Month: When “Month:” is displayed on the first line of the LCD, the second line shows the month. The default month is “January”, as shown in figure 5-6.

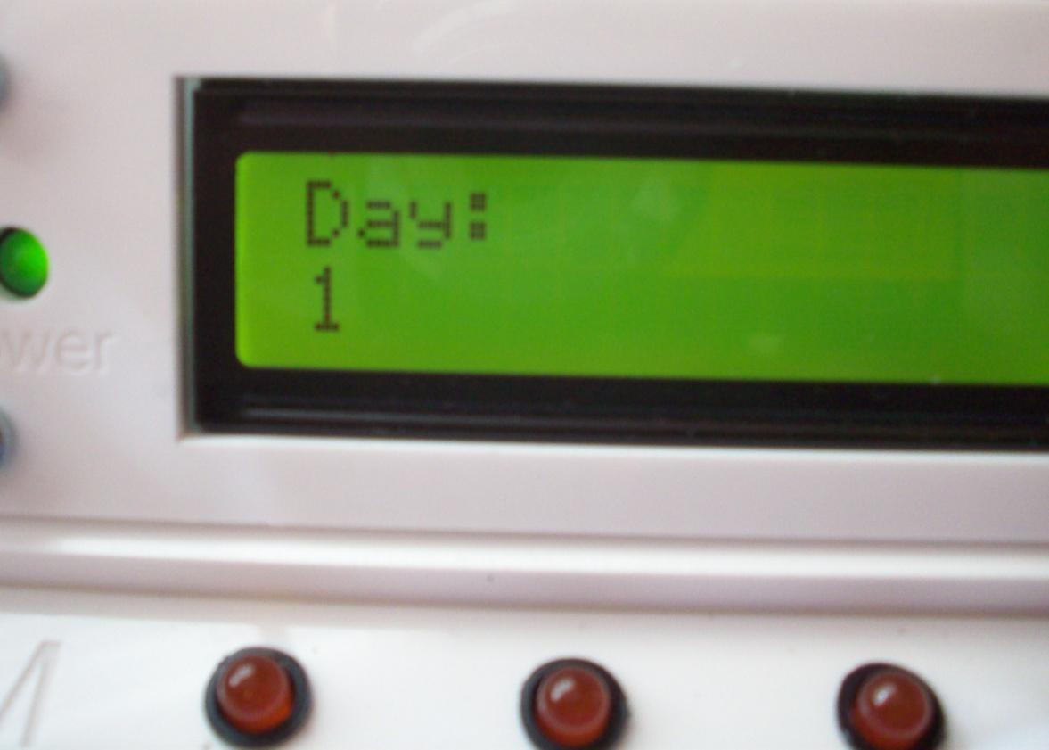
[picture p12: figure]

© 2014 Shrimpware LLC | Page 19

Figure 5-6. Month.

The Caregiver may press the INCREMENT button to advance the month forward, e.g. to February, March, etc. After December, the Month display will recycle back through January. After setting the month, the Caregiver presses SELECT to advance to “Day:”

- Day: When “Day:” is displayed on the first line of the LCD, the second line shows the day of the month. The default day is “1”, as shown in figure 5-7.

Figure 5-7. Day.

The Caregiver may press the INCREMENT button to advance the day forward, e.g. to 2, 3, etc. The Day will advance to 31 and then recycle back to 1. If the day is set higher than the number of days in the month, the actual day set in the Pill Reminder will be adjusted accordingly into the subsequent month; i.e. setting day 31 in April will result in an actual date set in the unit of May 1. After setting the day, the Caregiver presses SELECT to advance to “Hour:”.

- Hour: When “Hour:” is displayed on the first line of the LCD, the second line shows the hour on a 12 hour cycle (1 – 12). The default hour is “1”, as shown in figure 5-8.

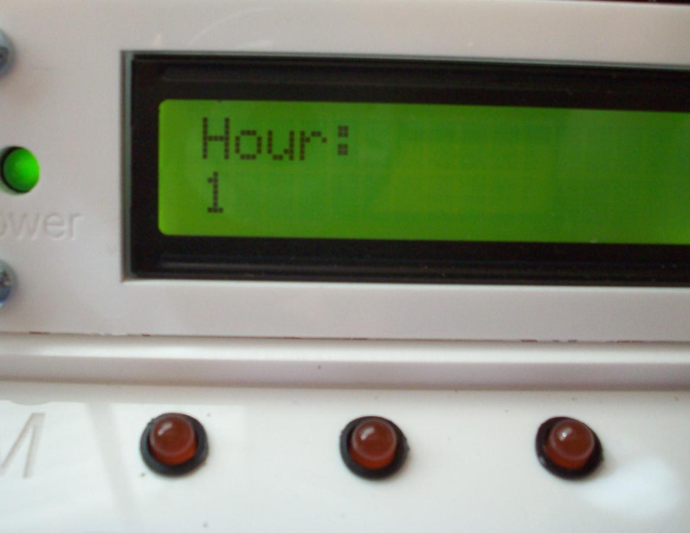
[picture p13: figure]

© 2014 Shrimpware LLC | Page 20

Figure 5-8. Hour.

The Caregiver may press the INCREMENT button to advance the hour forward, e.g. to 2, 3, etc. The Hour will advance to 12 and then recycle back to 1. After setting the hour, the Caregiver presses SELECT to advance to “Minute:”.

- Minute: When “Minute:” is displayed on the first line of the LCD, the second line shows the minute on a 60 minute cycle (0 – 59). The default minute is “0”, as shown in figure 5-9.

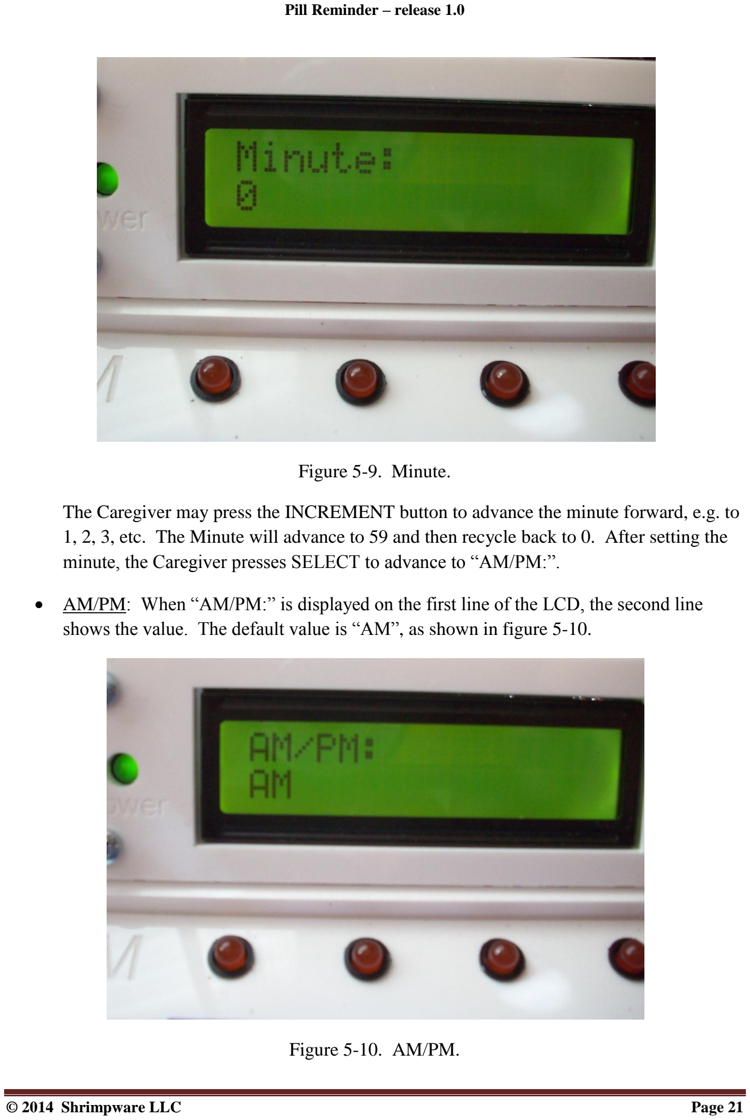
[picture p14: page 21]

© 2014 Shrimpware LLC | Page 21

Figure 5-9. Minute.

The Caregiver may press the INCREMENT button to advance the minute forward, e.g. to 1, 2, 3, etc. The Minute will advance to 59 and then recycle back to 0. After setting the minute, the Caregiver presses SELECT to advance to “AM/PM:”.

- AM/PM: When “AM/PM:” is displayed on the first line of the LCD, the second line shows the value. The default value is “AM”, as shown in figure 5-10.

Figure 5-10. AM/PM.

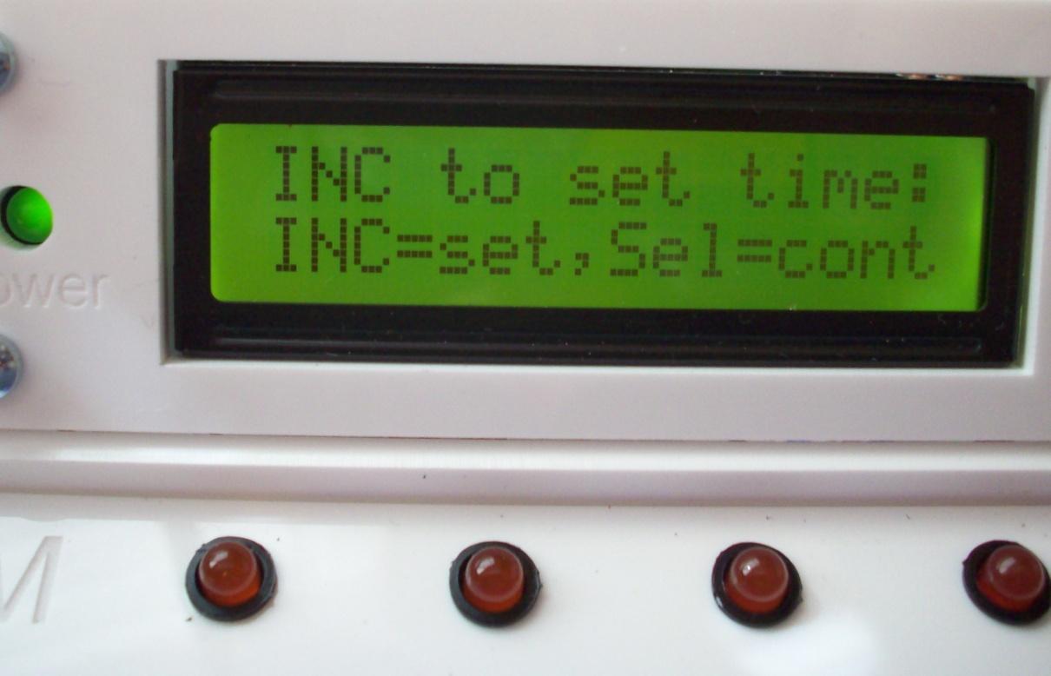
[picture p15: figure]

© 2014 Shrimpware LLC | Page 22

The Caregiver may press the INCREMENT button to advance to PM and then again to AM, etc.. After setting the AM/PM value, the Caregiver presses SELECT to advance to time setting.

- Time Setting: The LCD will display the options to set the time into the Pill Reminder or to recycle back to “Daylight Saving:” as shown in figure 5-11.

Figure 5-11. Setting the Date-Time.

At this point in the date time setting sequence, the Caregiver had made his/her selections but these selections have not been set within the Pill Reminder. With the LCD display showing figure 5-11, the Caregiver may press INCREMENT to set the selected date and time into the unit. At this point, the Pill Reminder will complete any of the Calibration time remaining and then enter normal operation, showing the date, day of week, and currently set time on the LCD display. If the Caregiver wishes to review and possibly alter his/her selections before storing them into the unit, s/he may press SELECT, which will recycle the LCD display back to “Daylight Saving:”. It is necessary to cycle through SELECT to this step once again in order to press INCREMENT to set the selected date and time into the unit and return it to normal operation.

Note: Pressing RESET at any time during the date-time setting cycle will return the Pill Reminder to the reset state and, after the 10 second calibration period, the Pill Reminder will display the current date and time based upon whatever was previously set in the unit. Therefore, the Caregiver can abort date-time setting without changing the previously time by pressing RESET before pressing INCREMENT at the point shown in figure 5-11.

© 2014 Shrimpware LLC | Page 23

5.4 Testing the Pill Reminder.

The Caregiver should, on a weekly basis, test the Pill Reminder for proper operation. In order to do this, the Caregiver should reset the unit, as described in section 5.2, above. The Caregiver should observe the Calibration and Self Test, paying particular attention to seeing that the LEDs light in sequence: Sunday AM, Sunday PM, Monday AM, Monday PM, etc. to make sure that all of the LEDs light up properly.

It does not matter which method the Caregiver uses to reset the unit – disconnect the power or open the cover and press the RESET pushbutton. However, when the Caregiver resets the unit in order to test it out, it is advisable for the Caregiver to stand on the side or in back of the unit so as to not trip the proximity sensor.

The proximity sensor may be tested by setting the date-time to any time that the Pill Reminder will light up an LED (i.e. any time between 6 am and noon, or between 6 pm and midnight). After the unit calibrates, the Caregiver can test the proximity sensor by moving in front of the unit. Tripping the proximity sensor will cause the lit LED to blink for approximately 4 seconds.

If the Caregiver set the date-time to test the proximity sensor, s/he must set the time properly before leaving the User’s facility. See section 5.3 for details. The Caregiver must always ensure that the Pill Reminder has the correct date and time set internally.

After intentionally tripping the proximity sensor, the Caregiver should once again reset the Pill Reminder and then get at least 5 feet way from the front of the unit within about 5 seconds of reset. This will ensure that the proximity sensor is armed for the next appearance of the User. In any event, the proximity sensor will automatically rearm the next time period that an LED is lit.

© 2014 Shrimpware LLC | Page 24

6 Specifications.

AC Power: 110 – 240 VAC, 50/60 Hz, 0.15 amp.

DC Power (power jack): 9 VDC at 0.65 amp.

Length: 10.75”

Width: 7.5”

Height (cover closed): 3.0” max.

Timekeeping Battery Life: 5 years, minimum

Replacement Battery: CR1632, 3 volt lithium coincell

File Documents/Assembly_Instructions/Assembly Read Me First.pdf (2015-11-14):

Page 1 of 6 | Copyright © Shrimpware LLC. All rights reserved.

## OVERVIEW OF PILL REMINDER

## ASSEMBLY INSTRUCTIONS

## Read this document before proceeding to purchase parts and assemble your Pill Reminder

Shrimpware LLC

Date: 5/13/14

1. OVERVIEW.

The Pill Reminder is assembled out of parts that are specified in the document “Pill Reminder Parts List” that can be found in the “Documents” folder of this release package. The sub-folder called “Assembly Instructions” contains a number of documents, each document providing details of a major step in the assembly of the Pill Reminder. The documents in this “Assembly Instructions” sub-folder are as follows:

- Pill Reminder Arduino IDE Installation: These instructions are needed to load the Pill reminder software into the Arduino Uno board that is part of the Pill Reminder electronics. Installing the Arduino IDE on your computer will also let you modify the open source Pill Reminder software if you so chose.
- Pill Reminder Shield Board Assembly Instructions. The shield board is a printed circuit board that you must assemble out of parts specified in the Parts List. Once assembled, the shield board plugs into the Arduino Uno board to form the bulk of the Pill Reminder’s electronics. This document contains step by step instructions for assembling the shield board.

NOTICE: Use of this document is subject to the terms of use described in the

document “Terms_of_Use_License_and_Disclaimer” that is included in this release package. This document can also be found at: http://www.shrimpware.com/pillreminder/TOU.html.

Page 2 of 6 | Copyright © Shrimpware LLC. All rights reserved.
- Pill Reminder Case Assembly Guide: This document provides step by step instructions for assembling the Pill Reminder enclosure out of pre-made parts that you can obtain from the Parts List. It also contains some instructions about making your own parts using
the CAD files supplied in the folder “Hardware | Enclosure CAD Files” out of raw wood
or plastic material and a laser cutter, should you desire to do so.
- Pill Reminder Final Assembly Instructions: This document contains the step by step instructions for completing and testing the Pill Reminder. You must first perform the steps in all of the documents listed above so that you have the completed piece parts ready for final assembly.

You may use these documents in any order except that the Pill Reminder Final Assembly Instructions must be the last set of instructions performed. The suggested order of assembly is to follow the order in which the documents are listed above.

You should read and review all of the above documents before ordering parts or otherwise investing time or money into building the Pill Reminder. It is your responsibility to make sure that you have the tools, skills and capabilities to undertake this project. Shrimpware LLC cannot provide technical support in the event that you get stuck and cannot complete any of these instructions without help. By proceeding to order parts and/or to perform any of the assembly instructions in any of these documents, you agree to assume all responsibility for the ensuring that you are capable of completing the project without help or assistance from us.

The following sections provide additional detail about each of these documents.

Page 3 of 6 | Copyright © Shrimpware LLC. All rights reserved.
2. Pill Reminder Arduino IDE Installation.

The Pill Reminder is powered by software that runs on an Arduino Uno microcontroller board. The software for the Pill Reminder is supplied in this release package under the “Software” folder. In order to get the software on to your Arduino Uno board, you must perform the following steps on your computer:

- Install the Arduino Integrated Development Environment (IDE) on your computer (Windows, Macintosh and Linux computers are supported). The Arduino IDE is downloadable free over the Internet.
- Install additional libraries into the Arduino IDE. The Arduino IDE comes with libraries, some of which are used by the Pill Reminder software. The Pill Reminder software requires additional libraries to be installed into your Arduino IDE. These additional
libraries are in the “Software | Libraries” subfolder of this release package and detailed
instructions for installing the libraries are included in this document.
- Load the Pill Reminder software into the Arduino IDE. This software is contained in the
“Software | Pill_Reminder_101” folder of this release package. The Pill Reminder
software is supplied to you as source code and (given that you have the skills and knowledge to do so), you are free to modify this software for your own, non-commercial use, in accordance with the license information contained in the “Terms_of_Use_License_and_Disclaimer” document that is in the top folder of this release package.
- Compile and verify the software and the correct software installation.
- Compile and upload the software to your Arduino Uno board. Once the software is uploaded to your Arduino Uno board, it is stored there in non-volatile flash memory and will remain on the board until it is overwritten.

The “Pill reminder Arduino IDE Installation” document provides step by step instructions to accomplish all of these tasks.

Page 4 of 6 | Copyright © Shrimpware LLC. All rights reserved.
3. Pill Reminder Shield Board Assembly Instructions.

You must assemble the “shield board”, which is a printed circuit board containing the electronics to connect various Pill Reminder components (LCD display, LEDs, PIR sensor and RTC module) to the Arduino Uno so that they may be controlled by the Pill Reminder software. The shield board is purchased off of the Parts List as a bare, 2 sided, printed circuit board. The Parts List contains ordering information for all of the parts that must be assembled onto the bare shield board. All parts are through-hole and require only a simple electronic assembly tools:

- Fine tip soldering iron and solder.
- Long nose pliers.
- Diagonal cutter.
- Wire stripper.

You should also have on hand a roll of electrical tape, insulated wire, and solder removal capability (e.g. solder wick, solder pullet). Some sort of “third hand” board holder and a magnifier may be helpful to have on hand as well. Further details of the tools and material required, as well as annotated step by step assembly instructions can be found in this document.

Page 5 of 6 | Copyright © Shrimpware LLC. All rights reserved.
4. Pill Reminder Case Assembly Guide.

You must assemble the Pill Reminder enclosure out of 2D parts that are cut from 3 mm wood or plastic stock. The parts list contains a link to order a kit of these parts, pre-cut for you, so that you only have to assemble them as instructed by this document. Alternatively, you can use the CAD files supplied in this release package to cut your own parts using a laser cutter. Further information about cutting your own parts is contained in this document. Regardless of how you obtain the enclosure parts, this document provides annotated step by step instructions for assembling them into the enclosure. Lots of photos are included and instructions are provided for making the enclosure out of wood as well as out of plastic. The material that you use is your choice and is discussed further in this document.

Assembly of the Pill Reminder enclosure requires a clean work area, wood glue (for wood) or solvent (for plastic) and bench clamps, rubber bands or other tools for holding parts together during assembly. It is also useful to have some small files on hand in order to make fine adjustments to the material during assembly.

Page 6 of 6 | Copyright © Shrimpware LLC. All rights reserved.
5. Pill Reminder Final Assembly Instructions.

This document contains annotated step by step instructions for completing and testing the Pill Reminder with the following, assembled parts on hand:

- Arduino Uno microcontroller board with the Pill Reminder software loaded on to it.
- Assembled shield board.
- Assembled enclosure.
- LED lamps, LCD module with cabling, PIR module with cabling, and RTC module with cabling.

You will also need the assembly hardware listed in the Parts List, which includes both metal and nylon screws, nuts, threaded standoffs, and insulated hookup wire. You will need an assortment of screw drivers, wire cutters and strippers, a soldering iron and solder (or crimp connectors and a crimping tool), pliers, and possibly some small files in order to complete the step by step instructions in this document.

We hope that you enjoy building and using the Pill Reminder.

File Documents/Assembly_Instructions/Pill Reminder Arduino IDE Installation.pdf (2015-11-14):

Page 1 of 7 | Copyright © Shrimpware LLC. All rights reserved.

## INSTRUCTIONS

## For Installation of the Arduino IDE and Libraries

## For Programming the Pill Reminder

Shrimpware LLC

Date: 4/21/2014

1. OVERVIEW.

The Pill Reminder software needs to be compiled and uploaded to the Arduino Uno board in order for the Pill Reminder to function. The Pill Reminder software and essential libraries are included with this release package in the archive file “Pill_Reminder_Release_Package_v1.zip”. After unzipping this archive, open the folder “Pill_Reminder_Release_Package_v1” and then the “Software” folder. There are two subfolders under “Software”: “Pill_Reminder_101” and “Libraries”. “Pill_Reminder_101” is the software that you need to compile and upload to the Uno board. Before this software will compile, the files under “Libraries” need to be installed into the Arduino Integrated Development Environment (IDE).

This document describes the steps necessary to:

1) Download and install the Arduino IDE on your computer.
2) Import the libraries included with this package into the Arduino IDE on your computer.
3) Compile and upload the software to your Arduino Uno.

It is recommended that you perform these operations before the Final Assembly of the Pill Reminder, as the Pill Reminder software contains self testing features that may be useful during final assembly.

NOTICE: Use of this document is subject to the terms of use described in the

document “Terms_of_Use_License_and_Disclaimer” that is included in this release package. This document can also be found at: http://www.shrimpware.com/pillreminder/TOU.html.

Page 2 of 7 | Copyright © Shrimpware LLC. All rights reserved.
2. DOWNLOAD AND INSTALL THE ARDUINO IDE.

Note: the Pill Reminder software has been developed under Arduino version 1.05. It is strongly recommended that you install this specific version on your computer, even if a newer version is available. Arduino 1.05 is the only version that the Pill Reminder has been tested with.

In order to install the Arduino IDE on your computer, open up your web browser software and go to:

http://arduino.cc/en/Main/Software

Find “Arduino 1.0.5” on this web page. Below this, you will see links for the following computers:

- Windows Installer, Windows (ZIP file)
- Mac OS X
- Linux: 32 bit, 64 bit
- source

Click on the link that matches your computer. If you have a Windows computer, you have the choice to either run the installer from the web page by clicking “Windows Installer” or downloading the installation package to your computer by clicking “Windows (ZIP file)”. It is recommended that you click on “Windows Installer”.

After clicking on the appropriate link for your computer, follow the instructions to install the Arduino IDE on your computer. You can safely ignore any warning messages about the software not being verified or registered. You can accept all defaults that are offered unless you have some reason to change them.

After you have successfully installed the Arduino IDE, you should see the Arduino icon on your desktop:

Double clicking this icon will open the Arduino IDE and show a window similar to the following:

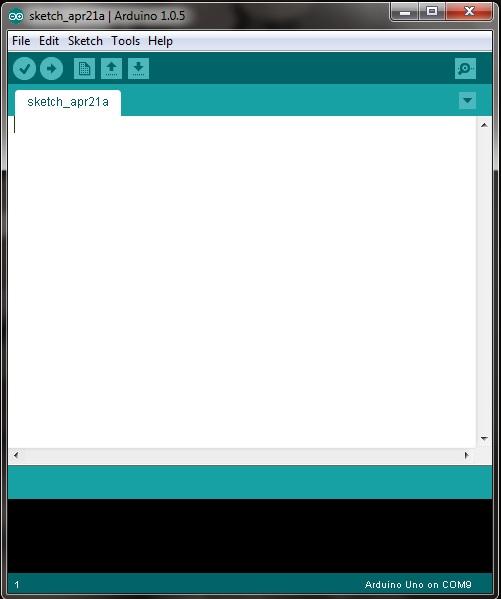
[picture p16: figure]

Page 3 of 7 | Copyright © Shrimpware LLC. All rights reserved.

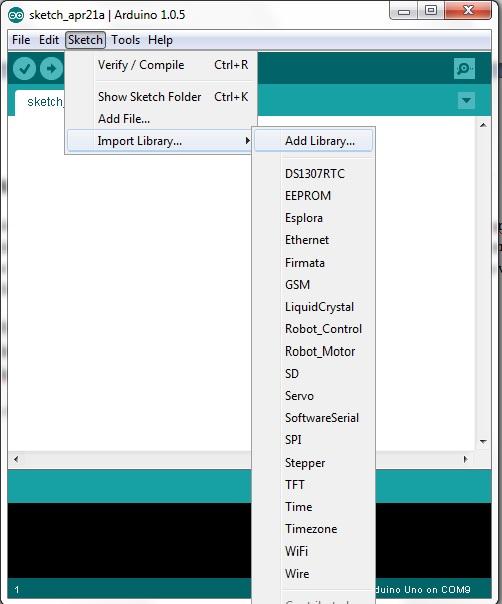
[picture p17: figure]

Page 4 of 7 | Copyright © Shrimpware LLC. All rights reserved.
3. INSTALL THE LIBRARIES INTO THE ARDUINO IDE.

The libraries that you need to install into the Arduino IDE are located in the unzipped archive: “Pill_Reminder_Release_Package_v1”. Open the “Software” folder. There are two subfolders under “Software”: “Pill_Reminder_101” and “Libraries”. Open the “Libraries” folder. You will see three subfolders:

- DS1307RTC
- Time
- Timezone

These are the libraries that you need to install.

With the Arduino IDE open on your computer, click on “Sketch”, then “Import Library”, then “Add Library”, as shown below:

Page 5 of 7 | Copyright © Shrimpware LLC. All rights reserved.

After clicking on “Add Library”, you will get a dialog box that allows you to navigate to the library folder that you wish to install. Recall that the libraries in your Pill Reminder release package are: “DS1307RTC”, “Time” and “Timezone”. After each of these libraries are added, they will appear under “Contributed Libraries” at the bottom of the list of libraries.

Note that the list of libraries may vary somewhat from the picture shown above. The libraries that must be in the list are as follows:

- Wire
- EEPROM
- LiquidCrystal
- DS1307RTC
- Time
- Timezone

You may need to close all Arduino IDE windows and reopen the Arduino IDE in order to see that the libraries have been properly installed.

It does not matter where in the list of Libraries these appear, as long as they all are in the list. If any are missing, the software will not compile.

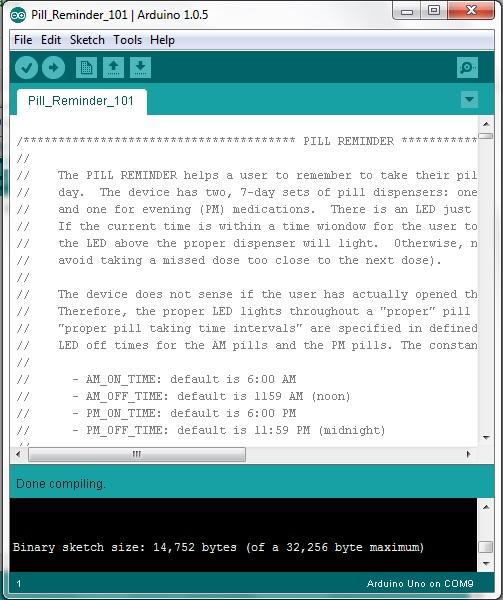
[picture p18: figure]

Page 6 of 7 | Copyright © Shrimpware LLC. All rights reserved.
4. INSTALL THE PILL REMINDER SOFTWARE INTO THE ARDUINO IDE.

With the Arduino IDE open, click on “File”, the “Open”, and navigate to the unzipped archive: “Pill_Reminder_Release_Package_v1”. Open the “Software” folder. There are two subfolders under “Software”: “Pill_Reminder_101” and “Libraries”. Open the “Pill_Reminder_101” folder and double click on the “Pill_Reminder_101” icon. This will open another Arduino IDE
window on your computer with the Pill Reminder software loaded into it. Now click “File”, then “Save” to save the Pill Reminder software into your Arduino sketchbook folder.

You can now test for successful installation of the software, the IDE and the libraries by clicking on the check icon at the top left of the IDE window (underneath “File”). A message on the green bar near the bottom will say “Compiling…” for a little while and then “Done compiling” if all is OK, similar to the picture below:

Page 7 of 7 | Copyright © Shrimpware LLC. All rights reserved.
5. UPLOAD SOFTWARE TO THE ARDUINO UNO.

Connect your Arduino Uno board to a USB port on your computer using the USB cable specified in the Parts List for the Pill Reminder. On a Windows computer, you will see some dialog about Windows finding new hardware and searching for a driver, etc. Just wait a little while, and Windows should finally say that it had found an Arduino Uno on COM <something>. <something> will be some number that is specific to your computer installation. Mac and Linux computers should likewise find and install the Uno automatically, albeit the messages will differ.

You must now close all Arduino IDE windows, and reopen the Arduino IDE. Click on “Tools”, then “Serial Port” and make sure that the serial port that your computer assigned your Uno to is
checked (if not, check it). Open the “Pill_Reminder_101” program using File | Open… and then
navigate to the “Pill_Reminder_101” icon. The program should reappear in the Arduino IDE window.

Click on the right arrow next to the check icon, below “File” on the Arduino IDE. The green bar near the bottom of the IDE window will first say “Compiling sketch…” for a little while, the “Uploading…” for a little while, and finally “Done uploading”. You have successfully compiled the Pill Reminder software and uploaded it you your Arduino Uno!

You can now unplug the USB cable from your computer and from the Arduino Uno.

NOTE: Once the software is in your Arduino Uno, it is located in flash memory and will remain in the Uno, even after power is removed from the Uno, until some other software is installed. Unless you install some other software on your Uno board, the Pill Reminder software will be loaded in its program memory and it does not need to be uploaded again. If, for some reason, you overwrite this software and need to reload it, you only need to repeat this last step #5 to do so. The Pill Reminder enclosure has a cutout for the USB connector on the Uno board so that future upgrades to the Pill Reminder software may be installed on the completed unit.

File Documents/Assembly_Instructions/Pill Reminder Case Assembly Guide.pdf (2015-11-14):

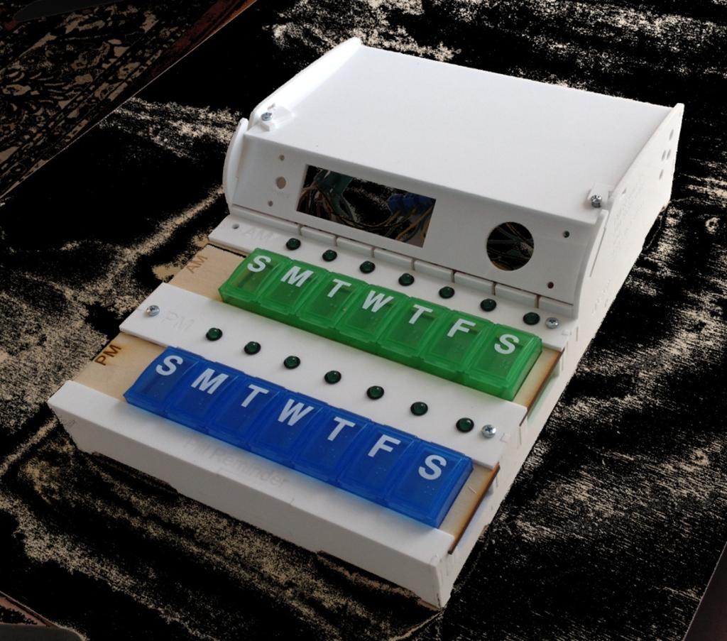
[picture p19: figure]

1 Of 17 | Copyright (c) 2014 Shrimpware LLC. All rights reserved.

# The Case for Your Pill Reminder

# Assembly Documentation

(Applies to Pill Reminder Case rev 19)

Document Revision 27 April 2014 Author: Jim Schrempp

NOTICE: Use of this document is subject to the terms of use described in the document “Terms_of_Use_License_and_Disclaimer” that is included in this release package. This document can also be found at: http://www.shrimpware.com/pillreminder/TOU.html.

2 Of 17 | Copyright (c) 2014 Shrimpware LLC. All rights reserved.

### Introduction

This document contains instructions for assembling the Pill Reminder enclosure. The parts list included in this release package (“Documents” folder) contains a link for ordering a kit of the pieces of the enclosure, precut for you. Alternatively, you can laser cut your own pieces using the CAD files
contained in the “Hardware | Enclosure CAD Files” folder in this release package.

The Pill Reminder enclosure parts can be cut from 3mm Baltic birch plywood for “cheap but cheerful” version, or out of your favorite color 3mm (0.118 inch) acrylic for the more “real product” look. In either case our advice is to always double check the fit of the parts BEFORE you glue them together. Once you're sure you have the right parts in the right places use just a little dab of glue to hold things together. With wood you'll have a chance to correct a mistake; with acrylic the glue (solvent really) is a final act.

These instructions are meant for use with any material you choose, and the photos will be of either material. The only real difference is in how you apply the plastic solvent or wood glue.

Note: We have found that acrylic sheets can vary in thickness from one manufacturer to another. The plans for the Pill Reminder case are made for 3mm material. If your acrylic is slightly thinner, the design will still work.

Be sure to check the web for updates and links to information about the Pill Reminder:

http://www.shrimpware.com/pillreminder

We hope you enjoy the project!

Shrimpware LLC

3 Of 17 | Copyright (c) 2014 Shrimpware LLC. All rights reserved.

### Parts List

For your project you will need:

| Description | Qty
1. | Pill Reminder Case plans | 1
2. 24x18 sheet of 3mm Baltic Birch plywood | or 24x18 sheet of 3mm acrylic plastic (recommended) | 1
3. | M3 metric machine screws, 10mm long | 18
4. | M3 metric nuts | 14
5. | 25mm hex standoffs with M3 threads | 4
6. Water resistant wood glue (ex Titebond III) | or Acrylic solvent – we prefer the more liquid kind
7. Philips screw driver

8.

9. | 12-inch padded bar clamp | 3

10.

11. | 7-Day pill dispensers – large size | 2 or 4
12.

13.

4 Of 17 | Copyright (c) 2014 Shrimpware LLC. All rights reserved.

### Before you begin

The Pill Reminder case is easy to assemble if you carefully follow the instructions.

However, if you're like me, then you will no doubt jump ahead, not read all the notes, and put glue where ever it makes sense. This strategy might work for you, but the glue is unforgiving once it sets. If you take this approach you might consider procuring a second set of parts right off the bat so that you can toss the first assembly and do it right the second time!

One way to improve your chances of a first success is to dry fit all the pieces, using some rubber bands to hold it all in place. A dry assembly allows you to see how everything goes together, look for any spots that might be tight so you can adjust them with a razor knife, or see some places where things go together in a way that you were not expecting. You might find yourself confused because our directions are not perfect – it's nice to resolve these issues before you have a load of glue dripping all over the place.

We strongly suggest putting the case together, then take it apart and do it a second time with the glue.

Once you have the case done you can fit the assembled electronics into it. Download the software and you should have a working Pill Reminder.

We wish you the best of luck!

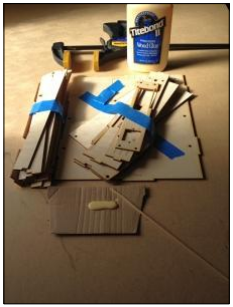
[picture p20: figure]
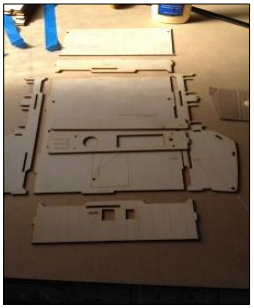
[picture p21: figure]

5 Of 17 | Copyright (c) 2014 Shrimpware LLC. All rights reserved.

### Step 1 Cut the Case Parts

Note: This step can be skipped if you purchase a kit of precut parts from the Parts List.

You will first need to cut out the parts. There may be other ways to do this, but we recommend using a laser cutter. CAD files in .cdr and .dfx formats are contained in the “Hardware | Enclosure CAD Files” folder of this release package.

One 24x18 inch sheet of any 3mm material should be enough to cut all the parts. It is important that the material be no more than 3mm thick; if not you will need to adjust all the tabs to fit the new material.

We recommend opaque acrylic, also known as Plexiglas; the cast material with the paper protection is best. We've found sheets of acrylic for as little as $14.00. At the same time, different vendors of “3mm” or “1/8 inch” actually supply sheets of different
thickness. As long as your acrylic sheet is 3mm or less then these
plans should work fine.

A cheaper choice is Baltic birch plywood as it is dimensionally true, is water resistant to a point, and can be finished easily.

Laser Cutters are a specialty tool, to be sure. If you don't know where to find one, you might look for a “maker space” in your area, such as the well known TechShop DIY shop. Alternatively, you could look for a commercial short run manufacturer in your area or the internet. Prawn Designs (www.prawndesigns.com) will also cut you a kit for a price.

We do not recommend cutting these parts by hand. You might be able to do it, but these plans are designed for precision cutting.

Once you have your parts, you're ready to go.

### Step 2 Lay Out the Parts

Place the main parts on a table in the correct orientation to be assembled.

Place the large piece with four tabs in the middle with the label “front” far away from you. The two complex figured side pieces appear to be the same, but one of them has a label “left” on it. Place that near the tab on the base that is also labeled “left”.

Note the cross piece labeled E is also laid out.

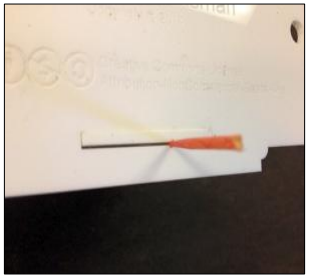
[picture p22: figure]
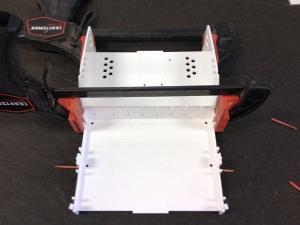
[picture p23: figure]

6 Of 17 | Copyright (c) 2014 Shrimpware LLC. All rights reserved.

### Step 3 Acrylic: Cement the Base Pieces Together

Find the Base, Left, Right, and E pieces. Note that the “E” on
the E piece should go towards the left side. Also note that the
arrow on the E piece must point up. Set the four pieces
together.

As mentioned earlier, your acrylic might be a tad thinner than 3mm. If so, you should use shims (e.g. broken toothpicks) to hold the base to the top of the slots as the solvent sets. See the photo to the right.

Place bar clamps or rubber bands in place to hold the parts as shown to the left. Position the clamps so that they are not on top of a tab.

Run a small bead of solvent across the lines where the parts meet the base. Don't put solvent where the tabs are – it will just run out.

Be sure to place a line of solvent to glue the E piece to the base.

Let your assembly sit for at least 5 minutes.

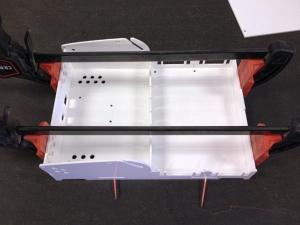
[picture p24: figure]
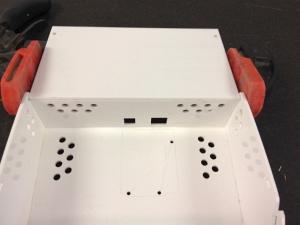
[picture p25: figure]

7 Of 17 | Copyright (c) 2014 Shrimpware LLC. All rights reserved.

Now place the front and back pieces on the base. Again use shims if your material is too thin. Reposition your clamps as shown to the right. Put small lines of solvent along the lines where the front and back meet the base.

Now place the flap door into the two holes at the back of the case and use a clamp to hold it in place as shown to the left.

Place solvent along the line where the back piece meets the side pieces. Be very careful to avoid getting any solvent into the hinge.

Wait at least 5 minutes for the solvent to begin to set.

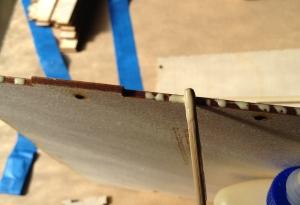
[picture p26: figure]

8 Of 17 | Copyright (c) 2014 Shrimpware LLC. All rights reserved.

### Step 3 Wood: – Glue the Base Pieces Together

If you're using wood then the work is a little
more involved. Using some kind of glue
spreader (e.g. a small stick), dab a bit of glue
along the “left” side of the big base. Don't put glue on the end of the tab.

With the complex side piece labeled “left” laying flat on the table, insert the base piece into the tab positions. You can see this in the background of the photo below.

Now apply glue to the piece marked E. Use a
dab of glue on the shoulder and a little swipe
of glue on either side of the tab.

Insert the E piece into the complex side piece where the slot is labeled “E”. Be careful to note the arrow on the E piece. This arrow should face AWAY from the base piece; in other words, when the box is assembled the arrow will be pointing “up”.

You now have one side piece with the base and piece E glued to it.

Apply glue to the free ends of the E piece and to the opposite side of the base piece. Carefully place the second side piece onto the base. You may have to jiggle the pieces a bit to get them all in, but take your time, it isn't hard to do.

Once you have your pieces assembled, locate the top flap door piece marked in one corner with a G. DO NOT apply glue to this piece. Carefully slip the two small tabs on this piece into the circular holes in the two side pieces. You will need to gently spread the two side pieces to fit this top flap on.

The Back Piece - Now locate the piece marked “back”. Note that it only fits one way. Place dabs of glue on the back edge of the bottom piece and on the tabs of the “back” piece. Fit the back piece to the case.

The Front Piece - Locate the piece marked “front”. Note that it only fits one way. Place dabs of glue on the front edge of the bottom piece and on the tabs of the “front” piece. Fit the front piece to the case.

At this point you should pause to let the glue dry a little bit. Sometimes the wood side pieces can be bowed a bit. You could use a bar clamp to hold them in place while the glue dries.

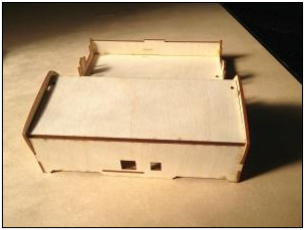
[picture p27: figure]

9 Of 17 | Copyright (c) 2014 Shrimpware LLC. All rights reserved.

Looking at it from the back, your box should now look like the photo below.

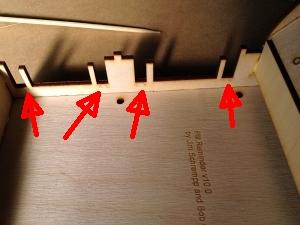
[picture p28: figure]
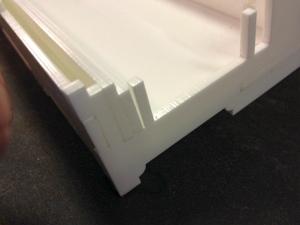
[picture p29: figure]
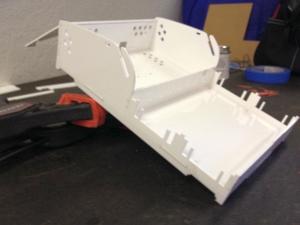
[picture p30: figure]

10 Of 17 | Copyright (c) 2014 Shrimpware LLC. All rights reserved.

### Step 4 The Cross Pieces Positions

Locate the two pieces labeled C, the two labeled D and the W, X, Y, and Z pieces.

Note that inside the left side piece are small labels indicating where these pieces belong. As you glue these pieces in place, be very sure that the side of each piece with the mark on it goes against the side of the case with the labels.

### Step 4 Acrylic: Cross Pieces

If you are using acrylic, then tip the case forward and place the C, W and D, Y pieces in place. Be sure the pieces are far forward in their slots and that they are seated completely down on the base.

The photo on the right above shows the C and W pieces in place, ready for application of solvent. Ensure that the C piece is nearest the front and the W piece is towards the back – this is very important! Note that they are both seated completely down in their position. Also note that this acrylic is thinner than 3mm and so there is a slight space to the back of the W piece. You can insert a shim here to hold the pieces in place while the solvent sets.

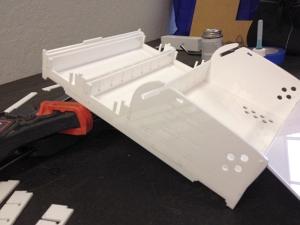
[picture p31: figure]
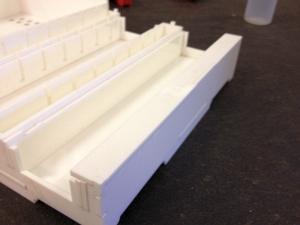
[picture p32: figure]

11 Of 17 | Copyright (c) 2014 Shrimpware LLC. All rights reserved.

Apply solvent across the line where piece W meets the base. Also apply a line where piece W and piece C meet. Repeat this with pieces D and Y. The D piece is nearest the front and the Y nearest the back.

Now tilt the case with the front up.

In this position you can now place the C, X and D, Z pieces in place. Use the letter on the left side of the case to guide your placement.

Use shims if needed and apply solvent as you did for the other cross pieces.

Allow the solvent to set for at least five minutes.

Lastly, apply the piece with the words Pill Reminder on it. This fits on top of the front piece. This is the most difficult piece to apply solvent cleanly. We recommend tipping the case up on its back and applying a sparse amount of solvent to the line between the loose piece and the front piece.

If you get solvent in places you don't want it, do NOT wipe it up. Your best result will be to just let the solvent evaporate; there will be some marring of the finish, but not much.

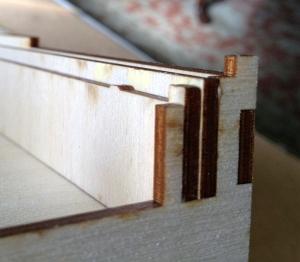
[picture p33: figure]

12 Of 17 | Copyright (c) 2014 Shrimpware LLC. All rights reserved.

### Step 4 Wood: Cross Pieces

Wood gluing is a bit more involved than acrylic.

C and W - Pick up the C and W pieces. Put some glue on the sides of each end of the C piece and place it in the slot closest to the front. Dab some glue all along the side of the C piece that is now towards the back of the case.

Pick up the W piece and place a small dab of glue on each side of each end tab. Press it into the slot next to the C piece. NOTE that the C piece should be nearest the front of the case. Look closely at the photo to the right.

Use your fingers to squeeze the sides of the two
pieces together so that the glue bonds them.

It is very important that each of these two pieces fit all the way to the bottom of the slot they are resting in. Check both sides and apply a clamp if needed.

C and X – Pick up the C piece you have placed
with the X piece. Apply glue as you did on the last C piece. Place it in the slot labeled CX with the C piece furthest to the back of the case. Now apply glue to the X piece and slide it in place next to the C piece.

Note in the photo at the right that the C piece is towards the back of the case and the X piece is about to be put into place.

Note that the X piece is not symmetrical. The end of the piece with the X goes to the left side of the case – also marked with an X.

Squeeze the two pieces together and make sure they are both pressed all the way into the slot.

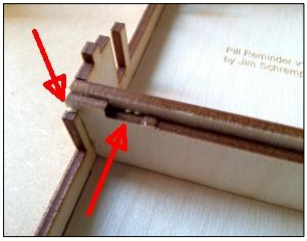
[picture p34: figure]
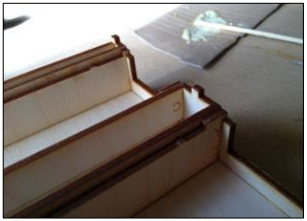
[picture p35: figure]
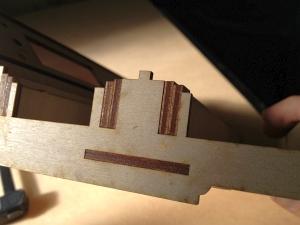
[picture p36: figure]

13 Of 17 | Copyright (c) 2014 Shrimpware LLC. All rights reserved.

Now is a good time to look for stray bits of wood glue. In the photo at the right you can see two places where little bits of glue have
squeezed out. In most parts of the case a bit of extra
glue doesn't hurt anything.

However, in the case of these cross pieces you should remove any little dabs of glue that you see.

D and Y – Repeat the process with the D and Y cross pieces. In this case the D piece goes into the slot in the position nearest the front, and the Y goes nearest the back.

The photo below shows the XC and DY pieces in place. Note that they are fully seated in the slots.

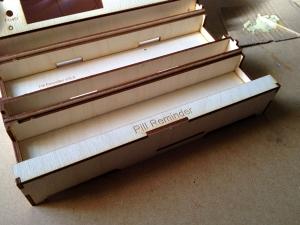
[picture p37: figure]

14 Of 17 | Copyright (c) 2014 Shrimpware LLC. All rights reserved.

D and Z – For the last time, repeat the process. With these two pieces, the D goes into the slot in the position nearest the back and the Z piece goes in nearest the front.

Now locate the top piece with the Pill Reminder
label on it.

Test fit the piece in place and note the parts of the case that it will rest on.

Place dabs of glue on the edges and place the piece in position. If the piece is warped you may need to use bar clamps to hold it in place while the glue dries.

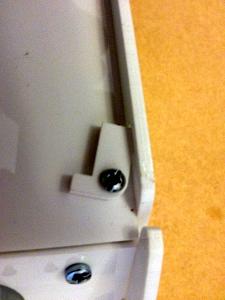
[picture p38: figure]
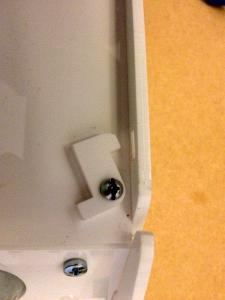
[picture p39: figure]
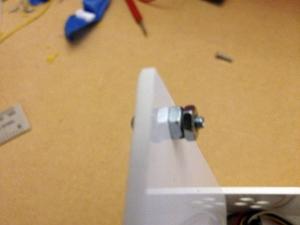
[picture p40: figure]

15 Of 17 | Copyright (c) 2014 Shrimpware LLC. All rights reserved.

### Step 5 Painting (optional)

If you want to paint your wood case, now is the time to do it. We recommend spray paint. If you want a smooth finish then paint, sand with 220 grit sandpaper, and paint again.

### Step 6 Top Flap Latches

Locate the two small latch dogs, two M3 screws, and four M3 nuts. Assemble the latches on the top flap as shown in the photo. Note that the dogs are not the same. They each have a small square etched into them. The etched square should be faced up when the dogs are in place.

Tighten the screws just enough to give friction to the latches. Then place a second nut on the screw. Tighten this nut against the first to keep the nuts from coming loose.

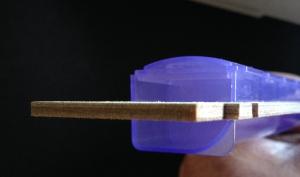
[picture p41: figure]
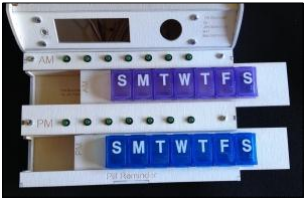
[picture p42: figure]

16 Of 17 | Copyright (c) 2014 Shrimpware LLC. All rights reserved.

### Step 7 The Pill Dispensers

Locate the pill dispensers and the two carrier slides, one labeled AM and one PM.

If you are using acrylic then you cannot press fit the dispensers – you will crack the slide carriers. One option is to cut your sliders from 3mm wood and use them. The other option is to use a file to increase the size of the hole in the carrier so that the pill dispensers fit easily. Then secure them with hot glue.

If you're using wood carriers, press one pill dispenser down into each carrier. Press them in only half way. The fit should be very tight. You may have to use a knife to scrape the slot in the carrier just a tad bit bigger to fit the variation in the size of your pill carrier. Or you might find that your pill carrier is a bit too small and slips through the slot; In this case you will need to glue your pill dispenser to the pill carrier. We suggest hot glue for this.

Now slide the AM and PM pill dispenser trays into the case. Note that the AM/PM label should be to the left.

The trays should easily slide in about 80% of the way. The last bit requires slightly more force and the trays will lock into place.

The trays can be removed by pushing them back to the right.

As a Caregiver, you may want to have two sets of pill dispensers and trays: one to leave with the User in the Pill Reminder and one to take home for you to reload with pills for the next week.

17 Of 17 | Copyright (c) 2014 Shrimpware LLC. All rights reserved.

### Step 8 Final Assembly

You have now completed the assembly of the Pill Reminder case. You need to complete the electronics assembly, and then do the final assembly where the electronics are mounted in the case.

Good luck!

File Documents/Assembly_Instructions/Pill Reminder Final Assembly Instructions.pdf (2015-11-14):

Page 1 of 26 | Copyright © Shrimpware LLC. All rights reserved.

## INSTRUCTIONS

## For Final Assembly of the Pill Reminder

Shrimpware LLC
Date: 4/29/2014 (v3)
1) TOOLS AND SUPPLIES.

Before beginning final assembly of the Pill Reminder, the following tools and supplies should be at hand:

a) Tools:
i) Soldering Iron
ii) Needle Nose Pliers
iii) Diagonal Cutter
iv) Wire stripper
v) Small (jeweler’s) straight screwdriver (for 3.5 mm screw terminals)
vi) Phillips and Straight Screw drivers
vii) Electrician’s tool (optional; for crimping die for #22 - #14 AWG wire crimp connectors)
b) Supplies:
i) Electrical solder
ii) Electrical tape
iii) Solder wick or solder remover
iv) #22 AWG stranded copper wire, insulated (two colors; green and yellow suggested)
v) 1/8 to 1/16 shrink tube insulation, about 14 inches.
vi) Shield PC board, assembled
vii) Enclosure, assembled except for display panel, LED panels, and cover latches
c) Optional:
i) Soldering iron stand

NOTICE: Use of this document is subject to the terms of use described in the

document “Terms_of_Use_License_and_Disclaimer” that is included in this release package. This document can also be found at: http://www.shrimpware.com/pillreminder/TOU.html.

Page 2 of 26 | Copyright © Shrimpware LLC. All rights reserved.

ii) PC board adjustable soldering stand iii) Magnifier
iv) Multi-meter

Page 3 of 26 | Copyright © Shrimpware LLC. All rights reserved.
2) ASSEMBLY INSTRUCTIONS, GENERAL INFORMATION.
a) Order of assembly.
i) Preparation.
ii) Display Panel Assembly.
iii) Sub-Assembly AM/PM LED Panels
iv) Assembly Instructions Electronics
v) Mounting the Arduino Uno and Shield Board.
vi) Combining Electronics and Case
vii) Dressing the wires and assembling the cover catches. viii)Testing.
b) Soldering.

Assembly requires that you have knowledge of skill of electronic soldering. A good tutorial on this subject can be found at:

https://learn.sparkfun.com/tutorials/how-to-solder---through-hole-soldering

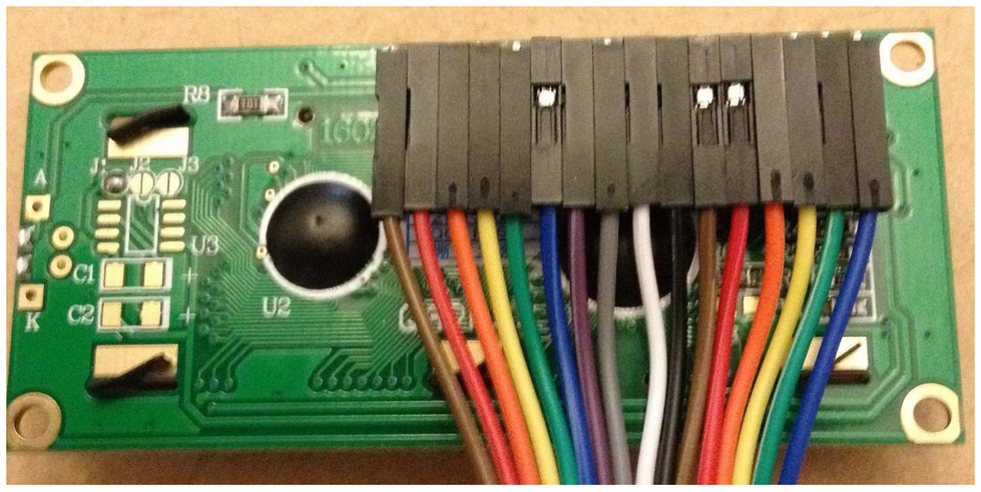
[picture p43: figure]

Page 4 of 26 | Copyright © Shrimpware LLC. All rights reserved.
3) ASSEMBLY INSTRUCTIONS, PREPARATION.
a) LCD

The LCD needs connection pins soldered on to it. The instructions are as follows:

Break off a 16 pin section from the breakable male header. Either the straight pin headers or the 90 degree angled pin headers can be used. Insert the short end of the 16 pin header through the holes at the top, back of the LCD module. Hold the pin header in place with some electrical tape and then solder the two end pins on the front side of the display. Then, solder the remaining 14 pins and inspect the solder connections. Remove the tape.

Take the 40 lead female-female ribbon cable and carefully count out 16 leads from either end. Tear off the 16 lead section to form a 16 lead ribbon cable.

Starting from pin 1 of the LCD header connector, insert each female connector, in order, from one end of the ribbon cable into each succeeding pin of the LCD male pin header, taking care to connect the wires in the order that they are in the ribbon cable. Figure 3-1 shows a completed LCD using an angle header (straight header is similar).

Figure 3-1. LCD with 90-degree header pins and cable.

Note: the cable is at the TOP of the LCD module.

b) Chronodot Realtime Clock (RTC) Module.

The RTC module needs the battery inserted and two pull-up resistors soldered onto it. The instructions are as follows:


Page 5 of 26 | Copyright © Shrimpware LLC. All rights reserved.

Insert the battery in the Chronodot, positive (+) side up. The battery slides into the battery holder from the front. Make sure that the battery is fully inserted into the battery holder.

The battery side of the Chronodot RTC has mounting holes for two pull-up resistors. Use 5.6K ohm resistors for both of these. Note that the module is made for 1/8 watt axial lead resistors which are hard to find. ¼ watt resistor leads will fit through the holes, but the resistor bodies are a little larger than the spacing provided and the leads need to be bent under the resistors to fit through the holes. It is acceptable to use ¼ watt resistors as long as care is taken not to short the bent leads to anything.

Insert the leads of two, 5.6K ohm axial lead resistors through the holes provided on the Chronodot with the resistors on the top (battery) side of the board. After inserting the resistor leads through the board, bend the leads on the back side of the board to hold the resistors in place. Carefully solder all 4 leads and inspect. Use diagonal cutters to clip off excess leads from the bottom of the module. The result should be as depicted in figure 3-2.

Figure 3-2. RTC with pull-up resistors added.

Note: The Chronodot comes with male pin headers already soldered in place.

Now, peel four female-female wire jumpers off of the 40 pin ribbon cable. Attach the left side RTC male pins to the Shield Board “RTC” connector pins, as follows:

Ground (bottom most pin in the RTC module) to Shield pin 1.

Vcc (next pin up on the RTC) to Shield pin 2.

SCL (next pin up on the RTC) to Shield pin 4. (Note: out of sequence!)

Page 6 of 26 | Copyright © Shrimpware LLC. All rights reserved.

SDA (next pin up on the RTC) to Shield pin 3. (Note: out of sequence!)

Note: Shield pins 5 and 6 are not connected.

c) LED connection “pigtail” wires.

Connection of the LEDs to the Shield Board requires that pairs of LED leads be soldered (or crimped) to “pigtail” leads. It is highly recommended that two colors of wires be used; e.g. green and yellow.

Cut 7 green wires and 7 yellow wires (14 total); each wire approximately 5 inches long.

Using a wire stripper, strip off approximately ½ inch of insulation from one end of each of the 14 wires. Strip of approximately 1/8 – 3/16 inch of insulation from the other end of each of the 14 wires. Inspect all wires to ensure a clean strip; i.e. no broken strands.

Put these “pigtail” wires aside for future use.

d) Programming the Arduino.

The Pill Reminder software should be programmed into the Arduino before assembly of the Pill Reminder. This will facilitate using the software to test individual steps during assembly. See the document “Pill Reminder Arduino IDE Installation” for details.


Page 7 of 26 | Copyright © Shrimpware LLC. All rights reserved.
4) ASSEMBLY INSTRUCTIONS, DISPLAY PANEL.

The display panel consists of a subpanel and a front panel, as shown in figure 4-1.

Figure 4-1. Sub-panel (top) and Front Panel (bottom).

Figure 4-1 shows the sub-panel (top) and the front panel (bottom), both as seen from the front of each panel. As depicted in the figure, the proximity detector (PIR) module mounts on the right, the LCD mounts to the left of the PIR and the POWER LED mounts to the left of the LCD. The PIR and LCD mount to the back of the sub-panel, which is then affixed to the front panel. The POWER LED mounts through the front of the front panel and through the sub-panel.

a) Mounting the PIR Module.

The PIR is mounted from the rear of the sub-panel. Insert two 2-56 nylon screws, 3/8” long, through the mounting holes on the front of the sub-panel and then through the mounting holes on the PIR. The PIR is mounted so that the cable connections are at the bottom and the two trim pots are at the top. Hold the PIR in place with 2-56 nylon nuts and tighten.

Note: Nylon screws and nuts should be used on electronic modules to preclude shorting.

It should not be necessary to adjust the pots. However, there is a jumper on the top, left side of the module (as viewed from the rear). Make sure that this jumper jumps the top two pins of the 3 pin jumper (the bottom pin is bare).

Tear a “ribbon cable” of 3 wires with female-female connectors from the 40 pin female-female ribbon cable. Place the three wires, in order, on the three male connector pins at the bottom center of the PIR module.


Page 8 of 26 | Copyright © Shrimpware LLC. All rights reserved.

Note: the PIR module comes with a 3 pin cable that has bare leads at one end. This cable is not used.

b) Mounting the LCD Module.

The LCD is mounted from the rear of the sub-panel. Note that the connectors are at the top of the module. Note also that there is a protrusion on one side of the module so that the LCD module can insert through the sub-panel only one way.

Insert four 4-40 nylon screws, 3/8” long, through the mounting holes on the front of the sub-panel and then through the mounting holes on the LCD module. Hold the LCD module in place with four 4-40 nylon nuts and tighten.

Note: Nylon screws and nuts should be used on electronic modules to preclude shorting.

c) Mounting the POWER LED.

The POWER LED is a green LED. It press fits through the front of the sub panel. The POWER LED is press fit into the sub panel. The fit is tight. Take care not to break the LED. If the fit is too tight, it may be necessary to gently file out the mounting hole. Take care not to file out the hole too much. The LED must fit snugly into the mounting hole. If you file away too much of the hole, a dab of hot glue can be used to hold the LED in place.

At this point, the sub-panel should look like Figure 4-2.

Figure 4-2. Sub panel with parts mounted.

d) Completing the Display Panel.

The front panel is attached to the sub-panel using four 4-40 machine screws (1/2 inch long) and eight 4-40 nuts. Place a machine screw through each of the four mounting holes on the front panel, from the front (where the LED shows). Now, place a nut on each screw and tighten down. These nuts act as spacers between the front panel and subpanel. The front panel should look like figure 4-3.


Page 9 of 26 | Copyright © Shrimpware LLC. All rights reserved.

Figure 4-3. Front Panel with mounting screws and nuts

Next, put the sub-panel through the mounting screws in back of the nuts, so that the LCD and PIR align with their cutouts in the front panel. Now attach the remaining four 4-40 nuts to the back of the screws and tighten. Figures 4-4 through 4-6 show the assembled front display panel, front and top views respectively.

Figure 4-4. Assembled Display Panel – Front View.

Figure 4-5. Assembled Display Panel – Top View.


Page 10 of 26 | Copyright © Shrimpware LLC. All rights reserved.

Figure 4-6. Detail view of sub panel attached to front panel


Page 11 of 26 | Copyright © Shrimpware LLC. All rights reserved.
5) SUB-ASSEMBLY INSTRUCTIONS, AM/PM LEDs.
a) Overview.

The LEDs press fit into the holes on the mounting panels. The leads of the AM LEDs are trimmed and the ends stripped. An AM/PM pair of LEDs (same day) are then wired “back to back” and soldered to the pigtail wires prepared in section 3 c), above. The groups of wires are soldered (or crimped) together and the ends of the pigtails attached to the shield board screw terminals.

Make sure to use a proper wire stripper on the proper stripping die (#22 AWG or larger).

b) Mounting the LEDs.

Seven amber colored LEDs are used for AM, and seven green colored LEDs are used for PM. Firmly, but gently, press each LED into its mounting hole in the AM and PM panels. It will help later on if you twist the leads for each LED together, as shown in figure 5-1.

Figure 5-1. LEDs Mounted in PM Panel with Twisted Leads.

c) Wiring the LEDs.

This step will require:

i) Trimming and stripping the leads from the AM LEDs ii) The “pigtail” wires prepared per section 3 c), above.
iii) Soldering iron and solder
iv) Shrink tubing
v) Jeweler's screwdriver for slotted head screws in Shield Board terminals.


Page 12 of 26 | Copyright © Shrimpware LLC. All rights reserved.

Identify the AM LED panel. Trim each of the leads from the AM panel LEDs to 3.5 inches long as shown in figure 5.3.

Figure 5-3. AM LED Leads Trimmed to 3.5 Inches

Use wire strippers to remove one-half inch of insulation from each of the fourteen wires.

In preparation for the next step, lay the AM LED panel on top of the PM LED panel and align the end of the LED leads as shown in figure 5-4.

Figure 5-4. The LED Panels Prepared for Soldering


Page 13 of 26 | Copyright © Shrimpware LLC. All rights reserved.

The first step is to identify the pair of AM LED leads that corresponds to each pair of PM LED leads. Start with the Sunday LED leads and bend the two pairs of leads upward so that they are obvious and distinct from the LED leads for all other days.

Next, identify the red lead of the AM LED for that day and the white lead of the PM LED for the same day. Wiggle the leads and look at the back of the LEDs to be sure that you have the correct wires. Take one of the green pigtail leads previously prepared and use the longer stripped end of the pigtail. Now, twist the red wire from the AM LED, the white wire form the PM LED and the green pigtail together. Twist these wires together well so that the bare leads are well connected and the insulation of all three wires starts at the same height.

Now identify the white wire from the PM LED and the red wire from the AM LED. Twist them together with the long stripped end of one of the yellow pigtail leads. Your work should look like figure 5-5.

Figure 5-5, The Sunday AM/PM LED Lead Pairs with Pigtail Wires.

Now solder the two twisted sets of wires together.

At this point, you have one pair of LEDs (an AM and PM LED for the same day) wired together with a green and yellow pigtail lead hanging free.

Repeat the above step with each of the other days. Be careful to always connect the LED leads of the same day together. Always connect the red lead of one LED with the white lead of the other. When you are done place a small piece of shrink tubing over each of the soldered groups and heat it to shrink it in place.

Starting with Sunday, identify the proper day of the week on the miniature screw terminals at the back of the Shield Board. Place the bare end of the green pigtail into the left side (as viewed from the front) of the 2 position screw terminal for the proper day of


Page 14 of 26 | Copyright © Shrimpware LLC. All rights reserved.

the week and use the jeweler’s screwdriver to tighten down the screw at the top of the screw terminal to hold the wire firmly in place. Make sure that the bare end of the pigtail is fully inserted into the screw terminal before tightening the screw and that no bare wire shows. After tightening the screw terminal, gently pull the pigtail outward to ensure that it is firmly gripped by the screw terminal. Next, repeat this step for the yellow pigtail into the right side of the same screw terminal.

After completing the AM and PM Sunday LED connections, repeat these steps for Monday … Saturday LED pairs, in order. Figure 5-6 shows a close up of the connections to the shield board. When done your assembly should look like figure 5-7.

Figure 5-6 LED Pigtails Attached to Shield Board


Page 15 of 26 | Copyright © Shrimpware LLC. All rights reserved.

Figure 5-7. LED Pigtails and Shield Board Assembly

d) Testing the LEDs.

Wiring up the LEDs is a complex procedure and it may help to test the first pair (Sunday) before proceeding on to the next pair of LEDs. To test your LEDs during assembly you will need to attach the shield to the Arduino board. At any time during this procedure, as any number of complete AM/PM pairs is wired, the LEDs may be tested as follows:

i) Make sure that all bare wires are bent away from the Shield Board.
ii) Plug the Pill Reminder “wall wart” power supply into an AC outlet and into the power connector on the back of the Arduino Uno board.
iii) The Calibration sequence should start up. This sequence flashes the Sunday AM LED, then the Sunday PM LED, then the Monday AM LED, then the Monday PM LED, etc. through the Saturday AM and PM LEDs. This sequence repeats four times. With only some LEDs wired up, you will have to wait for each of the cycles to go through the entire week before the cycle repeats (about 2.5 seconds per cycle). The four repeats should be sufficient to observe that the LEDs that have been wired up are connected correctly.


Page 16 of 26 | Copyright © Shrimpware LLC. All rights reserved.
6) ASSEMBLY INSTRUCTIONS, ELECTRONICS.

This section describes mounting the Arduino Uno, the Shield Board, and the RTC into the Pill Reminder enclosure.

a) Mounting the Arduino Uno.

Note: It is recommended that the Pill reminder software be programmed into the Arduino before assembly of the Pill Reminder. This will facilitate using the software to test individual steps during assembly. See the document “Pill Reminder Arduino IDE Installation” for details.

The Arduino Uno mounts into the enclosure electronics bay, under the cover, via three nylon screws. The holes for the screws are in the bottom of the enclosure, and the rear of the enclosure has cutouts for the power plug and the USB connector. See figure 6-1 for details.

Figure 6-1. Arduino Uno Mounted in the Enclosure.

The Arduino Uno has four mounting holes, but only three are used, as shown in figure 6-
1. Use three 4-40 Nylon screws, ½ inch long, to mount the Arduino Uno board. Place the three screws through the three holes on the Uno shown in figure 6-1. Place a 4-40 nylon nut on the back of each screw and tighten. These nuts serve as spacers between the bottom of the Uno and the bottom of the enclosure.

Now, place the three screws previously mounted to the Uno through the holes in the bottom of the enclosure. Place a 4-40 nylon nut on each screw and tighten. Place a second 4-40 nylon nut on each screw and tighten to lock the Arduino onto the enclosure.


Page 17 of 26 | Copyright © Shrimpware LLC. All rights reserved.
7) COMBINE LED SUB-ASSEMBLY WITH CASE

In this section you will add the LED sub-assembly to the Pill Reminder case.

a) Mounting the Standoffs

Before mounting the LEDs onto their respective panels, screw four metal 4-40 threaded standoffs, 25mm tall, into the enclosure, using metal 4-40 screws, ½” long.

Figure 7-1. One standoff in place. There are four to be installed.

b) Position the parts

Lay the LED sub-assembly on the case in the correct position. Be sure the AM LED panel is on top of the wires for the PM LED panel as shown in figure 7-2.

Figure 7-2. LED sub-assembly set in position.


Page 18 of 26 | Copyright © Shrimpware LLC. All rights reserved.
c) PM LED leads into place

Gently press the PM LED leads down into the slots provided. Near the bottom of each slot is a small bump that prevents the leads from coming back up the slot. You may need to use a small flat edged screw driver to gently push each wire past the bump. You will hear the leads “snap” into place. Figure 7-3 shows the PM LED leads in place.

Figure 7-3. PM LED leads are snapped in place

Now follow the PM LED leads towards the back of the Pill Reminder case and press the leads down into the next two sets of slots. Your assembly should now look like figure 7-4.


Page 19 of 26 | Copyright © Shrimpware LLC. All rights reserved.

Figure 7-4. PM LED leads are all in place.

Now gently work the PM LED bezel into place so that the two holes at the edges of the bezel align with the two standoffs in the case. Use two 4-40 screws to hold the bezel in place. Your Pill Reminder should look like figure 7-5.

Figure 7-5. PM LED bezel assembled into case

d) AM LED leads into place

Lower the AM LED bezel so that the LED leads can be added to the slots leading the back of the case. Gently press the leads from each LED into the back slots. There will


Page 20 of 26 | Copyright © Shrimpware LLC. All rights reserved.

now be four leads in each slot entering the back of the case. Gently work the AM LED bezel down into place and secure it with two 4-40 screws. Your case will look like figure 7-6.

Figure 7-6. LED bezels in place.

e) Attach Shield to Arduino

For the final step, move the LED leads and pigtails to the sides so that you can lower the shield on to the Arduino. The Shield Board press fits into the Arduino Uno using the female shield header connectors on the Uno and the male mates on the Shield Board. Carefully line up the pins on the assembled Shield Board with the header on the Uno board and press the Shield Board all the way into the Uno connectors (as far down as they will go). Your Pill Reminder should look like figure 7-7.


Page 21 of 26 | Copyright © Shrimpware LLC. All rights reserved.

Figure 7-7. LEDs and shield in place.


Page 22 of 26 | Copyright © Shrimpware LLC. All rights reserved.
8) ASSEMBLY INSTRUCTIONS, COMPLETION.

Place the assembled Display Panel into the grooves provided in the sloped front of the Pill Reminder enclosure. Make connections of the Chrondot, PIR, the LCD display, and the POWER LED as described below. Note: the Display Panel does not fasten to the enclosure. It sits in the grooves and is held into place by the top cover.

a) Mounting the Chronodot RTC Module.

The RTC module is mounted to the back of the enclosure via a nylon standoff and two nylon 4-40 screws (1/4” long). The back of the enclosure has a mounting hole to mount the standoff to the enclosure. The Chronodot RTC has a mounting hole that is used to mount it to the other end of the standoff. The RTC mounted into the enclosure and wired to the Shield Board is shown in figure 8-1.

Figure 8-1. Chronodot RTC Mounted and Wired to Shield Board.

Note: The pull-up resistors must be soldered to the RTC module prior to assembly – see section 3 b) above.

First, place a nylon 4-40 screw (1/4” long) through the back of the enclosure and screw down the 4-40 x ½ inch long double threaded standoff to it with the standoff inside of the enclosure. Then use another nylon 4-40 x ¼ inch long screw to attach the Chronodot RTC to the standoff, as shown in figure 8-1.

b) Wiring the PIR module.

From section 4 a), the PIR module has three wires with female pin header connectors ready for connection to the PIR connector on the Shield Board. The rearmost pin of the

Page 23 of 26 | Copyright © Shrimpware LLC. All rights reserved.

PIR Connector is marked “V” and gets connected to the “+5V” lead from the PIR module. The next pin is the signal and gets connected to the “OUT” lead from the PIR. The last pin is “G” and gets connected to the “GND” lead of the PIR.

c) Wiring the LCD module.

From section 4 b), the LCD Display module has a 16 wire ribbon cable with female pin header connectors ready for connection to the LCD connector on the Shield Board. Connect the 16 wires of the cable on the LCD to the 16 pins of the male LCD connector on the Shield board, one at a time, noting that pin 1 of the LCD is on the left end as viewed from the front and pin 1 on the Shield Board is the rearmost pin. Start with pin 1 and advance through the 16 pins in ascending order, making sure not to cross any wires (the pins on the LCD connect to the corresponding pins on the Shield Board LCD connector, in exact order).

d) Wiring the POWER LED.

From section 4 c), the POWER LED has a bare red and bare white wire hanging loose. Peel two wires off of the 40 wire female-female ribbon cable and press a bare wire from the LED into one end of each female-female cable. The cable connected to the red LED wire is then plugged into the “A” pin on the “PWR LED” connector on the Shield Board. The cable connected to the white LED wire is plugged into the “C” pin on the “PWR LED” connector on the Shield Board.

e) Dressing the Cables.

The wiring of the Pill Reminder is now complete. Stick-on cable tie holders and cable ties should be used to dress the wires neatly and securely inside the Pill Reminder electronics bay. Refer to figure 8-2 for ideas about dressing the wires.


Page 24 of 26 | Copyright © Shrimpware LLC. All rights reserved.

Figure 8-2. Dressing Wires for Final Assembly.

f) Assembling the Top Fasteners.

The last items to assemble are the catches that are used to keep the electronics bay cover closed whenever the Caregiver does not need to access the electronics. Each cover catch is secured to the cover via a 4-40 machine screw (3/8” long) and two nuts. It is suggested that the first nut be metal and the second nut, used to secure the nuts from falling off, be nylon. Note that the two catches are slightly different. Figure 8-3 shows the catches with their paper cover still attached. You will note that there is an etched portion on each catch. That bit should be face up when the catches are attached to the case top.

Figure 8-3. Left catch and Right catch

Figure 8-4 shows the assembled catch in the closed and locked position (left) and in the open position (right). When assembling the cover catches to the electronics bay cover,


Page 25 of 26 | Copyright © Shrimpware LLC. All rights reserved.

make sure that the catches are loose enough to move easily and that they each seat properly in their respective slots in the side of the Pill Reminder enclosure.

Figure 8-4. Cover Catches, Properly Assembled.

Page 26 of 26 | Copyright © Shrimpware LLC. All rights reserved.
9) TESTING.

The Pill Reminder software provides a self test of the LEDs at the startup and calibration time. After calibration, the unit displays the date, day and time on the LCD and will blink a lit LED the first time that the PIR is tripped after calibration (assuming that the time is appropriate for an LED to be lit). Complete instructions for testing the Pill Reminder can be found in the document “Pill Reminder User Manual”, section 5.4.

Set the date and time into the Arduino as described in the “Pill Reminder User Manual”, section 5. Then, unplug the power for 5 seconds and reconnect power. After about 10 seconds of “Calibrating …”, the LCD should display the correct date, day and time. If so, you have successfully completed assembly up to this point.

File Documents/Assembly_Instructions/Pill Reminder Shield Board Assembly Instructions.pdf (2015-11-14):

Page 1 of 16 | Copyright © Shrimpware LLC. All rights reserved.

## INSTRUCTIONS

## For Assembly of the Pill Reminder Shield Board

Shrimpware LLC
Date: 3/05/2014
1) TOOLS AND SUPPLIES.

Before beginning assembly of the shield board, the following tools and supplies should be at hand:

a) Tools:
i) Soldering Iron
ii) Needle Nose Pliers
iii) Diagonal Cutter
iv) Wire stripper
v) Small (jewelers) straight screwdriver (for 3.5 mm screw terminals and trim pot)
b) Supplies:
i) Electrical solder
ii) Electrical tape
iii) Solder wick or solder remover
iv) #22 AWG solid copper wire, insulated
v) Shield PC board
vi) Shield parts kit (see parts list)
c) Optional (see photo 1, below):
i) Soldering iron stand
ii) PC board adjustable soldering stand iii) Magnifier
iv) Multi-meter

NOTICE: Use of this document is subject to the terms of use described in the

document “Terms_of_Use_License_and_Disclaimer” that is included in this release package. This document can also be found at: http://www.shrimpware.com/pillreminder/TOU.html.


Page 2 of 16 | Copyright © Shrimpware LLC. All rights reserved.

Photo 1. PC Board Adjustable Soldering Stand and Multimeter.


Page 3 of 16 | Copyright © Shrimpware LLC. All rights reserved.
2) ASSEMBLY INSTRUCTIONS.
a) Soldering. Assembly of the Shield Board requires that you have knowledge of skill of electronic soldering. A good tutorial on this subject can be found at:

https://learn.sparkfun.com/tutorials/how-to-solder---through-hole-soldering

b) General instructions: Before beginning assembly, please read through and understand these general instructions:
i) All parts are mounted on the top side of the board. The top side of the board is the side with the silk screen printing on it – see photo 2, below.

Photo 2. Top Side of Blank Shield Board.


Page 4 of 16 | Copyright © Shrimpware LLC. All rights reserved.

Photo 2a. Shield Board with Major Parts Identified.

ii) All parts are soldered on the bottom side of the board only.

iii) The following parts have rigid pins and do not grip the board to hold the part in place when the board is inverted to solder the pins on the bottom. It is recommended to place the part on the top of the board, align the part as necessary, and apply electrical tape to hold the part in place for soldering. As soon as the board is inverted for soldering on the bottom side, solder the two pins at opposite ends (diagonally, in the case of the DIP socket) first to hold the part rigidly. Then solder the remaining pins to the board.

(1) 0.1” male pin headers. Care must be taken to keep these parts in vertical alignment as they tend to tilt sideways because they are loose in the holes in the board. Place these parts into the holes so that the short pin ends protrude through to the bottom of the PC board. Align each connector vertically and use electrical tape to hold it firmly into the holes, with the plastic center pieces firmly seated

Page 5 of 16 | Copyright © Shrimpware LLC. All rights reserved.

into the top side of the PC board and the connector straight up and down and not slanted sideways.

(2) Arduino headers. The headers require extreme care to ensure that they are fully seated on the PC board and absolutely vertical when they are soldered into place. After assembly, they must fit into the Arduino without undue stress and strain. The same techniques apply as for the 0.1” pin headers, above. Extra care and diligence is advised.
(3) DIP socket. The DIP socket is easier to solder since it has two rows of pins that will prevent it from tilting. However, it should be taped or otherwise affixed to the top side of the PC board so that it stays in place when the board is inverted for soldering.

iv) The three pushbutton switches have pins that are bowed outward to snap into a PC board. Once inserted into the PC board properly, the pins will hold the pushbuttons in place when the board is inverted for soldering. Care must be taken to ensure that the pushbuttons are inserted into the PC board in the proper orientation. The underside of the pushbuttons has a plastic line between sets of two pins. These pins are shorted together. They should align front to back of the PC board. The pins make contact with the conductors on the PC board even before they are soldered into place. It is recommended to check for proper alignment with a multimeter before soldering the pushbuttons into place. See the assembly instruction details for this step in the Shield assembly for further details.

c) Inspect PC shield board for damage and deburr edges.
i) File down any burs on the board edges to avoid cuts and scrapes
ii) Visually inspect the board for any damage or defects, such as:
(1) Breaks in conformal coating, except for solder pads and vias.
(2) Ensure that holes are drilled in the center of each component solder pad.

iii) Place the multimeter in resistance measurement and check that there is an open circuit between the Arduino connecter pin labeled “+5V” and any one of the Arduino pins labeled “GND”. Refer to photo 2, above, for details. If there is not an open circuit between these contacts on a bare shield board, then the board has a power short and should not be used.

d) Solder 0.1” male pin headers to the PC board.
i) If necessary, break the long 0.1” spaced pin header strips into individual connectors, as follows, per photo 3, below:
(1) One 16 pin header
(2) One 6 pin header
(3) One 3 pin header


Page 6 of 16 | Copyright © Shrimpware LLC. All rights reserved.
(4) One 2 pin header

Photo 3. Male Pin Headers for Shield Board

ii) Place the 16 pin header into the “LCD” connector holes in the Shield Board, as shown in photo 4, below:

Photo 4. LCD Pin Header Placement on Shield Board.

iii) Use electrical tape to hold the pin header in place and vertical, as shown in photo 5, below.


Page 7 of 16 | Copyright © Shrimpware LLC. All rights reserved.

Photo 5. Tape Holding Pin Header in Place for Soldering.

iv) Invert the shield board and solder the two end pins first to hold the connector in place. Then solder the remaining pins.

e) Repeat this procedure for:
i) 2 pin header (Power LED) ii) 6 pin header (RTC module)
iii) 3 pin header (PIR module).

See Photo 6 for completed pin headers.

Photo 6. Pin Headers Soldered on Shield Board.

f) Solder Arduino header connectors to PC board. The Arduino header connectors are shown in photo 7, below. They are placed per photo 2a, above. NOTE: the Arduino header pins must be straight vertically and must be in a line with each other, or else they will not mate properly with the Arduino Uno board. Two methods to achieve this are described below.


Page 8 of 16 | Copyright © Shrimpware LLC. All rights reserved.

Photo 7. Arduino Headers.

i) Method 1: Place the headers, one at a time, into the proper holes in the Shield board. Use electrical tape to secure the header in place. Invert the board and make sure that the metal pins are vertical, perpendicular to the board. For the second connector on each side, make sure that the pins are in absolute alignment with the pins on the connector just in front or in back of it. Solder the two pins at each end to hold the connector in place; then solder the remaining pins. Repeat this step for each of the 4 headers.

ii) Method 2: Put all 4 headers through the proper holes in the shield board and plug the metal ends into an Arduino Uno board, so that the header pins are well seated into the mating connectors on the Arduino. Using electrical tape, tape the shield board up flush against the plastic body of all for connectors. Glue the insides of the plastic connectors to the shield using a hot glue gun or other glue compatible with plastic. Let the glue dry thoroughly. Carefully unplug the shield, invert the shield board and solder the end pins of each connector to hold them in place. Then solder the remainder of the pins.

With either method, check for proper seating of the shield into an Arduino before proceeding on to the next steps. If a connector has to be removed, it is best to use diagonal cutters to cut through the plastic body of the header and then use solder wick or a solder removing tool to remove as much solder as possible from each pin. Use long nose pliers and the soldering iron to loosen the remaining solder on each pin and remove the pins, one at a time using solder wick or solder removal tool to clean and solder out of the mounting holes on the shield board. Note: removal of the Arduino headers is very difficult and extreme care should be taken in this assembly step to ensure that it is done correctly the first time! After completing this step, the shield board should look like photo 8.


Page 9 of 16 | Copyright © Shrimpware LLC. All rights reserved.

Photo 8. Arduino Headers Mounted on Shield Board Plugged into an Arduino.

Unplug the shield board from the Arduino after the header pin alignment test.

g) Solder screw terminal connectors to PC board. There are 7, two-position, 3.5mm screw terminals that need to be soldered to the rear of the shield board, as indicated on photo 2a, above. Starting with either end (SU or SA), place a screw terminal through the holes at the top of the board so that the wiring terminals point outward from the rear of the board. Use electrical tape to hold the screw terminal fast to the top side of the board and in neat alignment with the rear of the board. Invert the board and solder both leads. Repeat the procedure for the remaining six screw terminals, one at a time.
h) Solder 16 pin DIP socket to PC board. Place the 16 pin dual in-line (DIP) socket into the top of the board, as indicated in photo 2a, above. Use electrical tape to hold it fast to the board. Invert the board and solder two pins at diagonally opposite ends of the socket to hold the socket in place. Then solder the remaining pins on the socket.
i) Place and solder (3) pushbutton switches. Locate the position of three pushbutton switches on photo 2a, above. The pushbuttons have pins that are bowed outward to snap into a PC board. The pushbutton pins are spaced wider in one direction than the other, so the pins should align only one way. Do not force the buttons into the board. Make sure that pin alignment is correct. Another check is to look at the bottom of each pushbutton. The pairs of pins that are shorted together inside each switch is denoted by a line in the plastic connecting pairs of pins. These plastic lines should be aligned front to back of the shield board (not side to side). Once each pushbutton switch is inserted into the shield board, check for correct alignment using the resistance setting on the multimeter as follows:
i) RESET: Place one lead of the multimeter to the “RST” pin of the Arduino power header and the other lead to a “GND” connection on the same Arduino header. The multimeter should read an open circuit. Push the RESET button and the multimeter should read a short circuit while the button is depressed. Once tested correctly, invert


Page 10 of 16 | Copyright © Shrimpware LLC. All rights reserved.

the board and solder all 4 pins of the RESET button pins in place, and recheck with a multimeter as described above.

ii) INCREMENT: Place one lead of the multimeter to Arduino pin “D2” on the lower Arduino digital header, and the other lead to a “GND” connection on the Arduino power header. The multimeter should read an open circuit. Push the INCREMENT button and the multimeter should read a short circuit while the button is depressed. Once tested correctly, invert the board and solder all 4 pins of the INCREMENT button pins in place, and recheck with a multimeter as described above.

iii) SELECT: Place one lead of the multimeter to Arduino pin “D3” on the lower digital Arduino header, and the other lead to a “GND” connection on the Arduino power header. The multimeter should read an open circuit. Push the SELECT button and the multimeter should read a short circuit while the button is depressed. Once tested correctly, invert the board and solder all 4 pins of the SELECT button pins in place, and recheck with a multimeter as described above.

After this step, the Shield Board should look like photo 9, below:

Photo 9. Shield Board with Screw terminals and Pushbuttons Attached.

j) Place and solder 10Kohm trim potentiometer. Locate the 10K ohm potentiometer (trim pot). The trim pot leads are arranged in a triangle. The trim pot pins are aligned with the shield board as shown in photo 9, under the word “CONTRAST”. In order for the trim pot to fit properly on the board, the center pin (apex of the triangle) needs to be


Page 11 of 16 | Copyright © Shrimpware LLC. All rights reserved.

bent outward from under the pot and then down to fit where the hole in the shield board is. Use long nose pliers to make the bends. See photo 10 for details.

Photo 10. Trip Pot with Bent Wiper Lead.

Insert the trim pot into the board and bend the leads from the underside of the board to hold the trim pot in place. Solder all three leads. Clip off the excess leads using diagonal cutters after soldering. After soldering in the trim pot, it should look like photo 11.

Photo 11. Trim Pot Soldered on Shield Board.

In order to test the trim pot, put the multimeter on a resistance setting. Place one lead of the multimeter to LCD pin 3 (third pin down from the front of the 16 pin male pin header labeled “LCD”). Place the other lead of the multimeter to one of the “GND” pins of the Arduino power header. Rotate the pot control with a jeweler’s screwdriver and observe zero ohms at one extreme of pot rotation and approximately 10K ohms (10,000 ohms) at the other extreme end of the rotation. Move the multimeter lead from “GND” to “+5V” of the same Arduino power header and observe the opposite effect (zero and approximately 10K ohms at the opposite ends of pot rotation). Leave the pot


Page 12 of 16 | Copyright © Shrimpware LLC. All rights reserved.

approximately in the center of its rotation at this time. If these readings are not observed, then the pot is installed incorrectly or is bad.

k) Place and solder the 100 uf electrolytic capacitor. Locate the electrolytic capacitor. The electrolytic capacitor is mounted in the circular outline at the lower left hand end of the board shown in photo 2a, above. The round hole is for the negative side and the square hole is for the positive side. The negative lead is shorter and has a silver stripe on the body of the capacitor. The positive lead is longer and does not have the stripe on the capacitor body. Electrolytic capacitors are polarized and it is important to mount the positive and negative leads correctly. With the device in the proper orientation, insert the leads through the holes and bend them on the underside of the board to hold the device in place. Then solder the leads. Clip off excess leads above the solder joints with a diagonal cutter. The board should look like photo 12, below.

Photo 12. Shield Board with Electrolytic Capacitor Installed.

l) Place and solder (2) 0.1 uf ceramic capacitors. There are two, 0.1 uf capacitors to be mounted. One is mounted to the right of the IC (the 16 pin DIP socket). The other is mounted just to the back (left) of the electrolytic capacitor. Refer to photo 2a, above. These devices are not polarized and can be inserted in any direction. Place the leads through the holes in the board, bend the leads on the bottom side of the board to hold the capacitors in place, invert the board and solder the leads. Clip off excess leads with diagonal cutters.
m) Place and solder 2N2222 transistor. The transistor mounts in a “D” shaped area below the DIP sockets, as shown in figure 2a, above. The transistor has a “D” shaped cross section and the three leads of the transistor must be placed in the holes in the board such that the cross section matches the “D” pattern in the silkscreen. Insert the transistor leads in the holes on the board and bend the leads back on the underside of the board to hold the transistor in place. Invert the board and solder the leads. Use a diagonal cutter to clip off the excess leads above the solder joints.

Page 13 of 16 | Copyright © Shrimpware LLC. All rights reserved.
n) Place and solder (2) 5.6Kohm axial lead resistors. Two 5.6K ohm resistors mount (1) below and (2) next to the transistor, as shown in figure 2a, above. Resistors are color coded as to their value, but it is best to check them with the resistance setting on your multimeter to make sure that you place the right parts in the right locations. The value read on the multimeter will not be exactly the specified value; it may typically vary from the specified value by +/- 5% or so. Resistors are not polarized. Bend the leads on either side of each resistor so that the resistor body lies flat on the board when the leads are inserted fully through the designated holes. Bend the leads back on the underside of the board to hold the resistors in place. Invert the board and solder the resistor leads. Clip off excess lead wire with a diagonal cutter.
o) Place and solder 560 ohm axial lead resistor. One 560 ohm resistor is mounted directly below the 5.6K ohm resistor that is below the transistor. Refer to photo 2a for details. Check the 560 ohm resistor with a multimeter and then mount it to the board in the same manner as for the two 5.6K ohm resistors, above.
p) Place and solder (8) 330 ohm axial lead resistor or wire shunt. The Shield Board has provision to mount eight 330 ohm resistors. Seven of these are near the screw terminals and one is near the transistor below the DIP socket. These resistors are current limit resistors for the 7 AM/PM LED pairs and one for the power LED. If the LEDs that you are using have internal resistors, then it is necessary to solder a piece of #22 - #26 wire in these resistor locations. The resistor values can also be varied depending upon the type and desired brightness of the LEDs.

The resistors are mounted to the shield board in the same manner as the 5.6K ohm and 560 ohm resistors, above. In the event that the LEDs have internal resistors, prepare and solder in a “shunt” wire in each resistor location. A shunt wire is a piece of wire where about 0.7 cm of insulation is left on the wire, as shown in photo 13, below. The bare leads are bent 90 degrees from the insulated body and inserted through the holes where resistor leads would normally go. They are soldered to the board in the same manner as if the wire were a resistor.


Page 14 of 16 | Copyright © Shrimpware LLC. All rights reserved.

Photo 13. Shunt Wires, for LEDs with Internal Resistors.

q) Inspect the board. Carefully inspect all solder joints for good solder flow and no shorts. Make sure that there is adequate solder on each joint and that there are no cold joints. Clean off any debris from the bottom of the board with a clean cloth and/or compressed air.
r) Insert the 74HC595 IC into the 16 pin DIP socket. Pin 1 on the socket faces the front of the PC board. Pin 1 on the IC may be denoted with an indented dot on the package near one corner pin of the IC. Alternatively, the pin 1 side of the IC may have a “U” shaped notch in the package. Photo 14 shows placement of the IC in the socket where pin 1 is denoted with the U shaped notch.


Page 15 of 16 | Copyright © Shrimpware LLC. All rights reserved.

Photo 14. Shift Register Placement and Orientation

Note that the pins of a DIP IC usually flare outward from the package and may need to be bent inward in order to fit into the socket. This can be done by placing the IC sideways on a rigid flat surface so that one side of pins is flat on the surface. Grasping the plastic top and bottom of the IC package only, gently rotate the package upward so that the pins on the flat surface bend to a 90 degree angle with the package. Repeat the produce for the pins on the opposite side of the IC. The IC should then insert directly into the socket. Inspect carefully to make sure that all of the pins are in the socket and that none are bent under the IC.

Page 16 of 16 | Copyright © Shrimpware LLC. All rights reserved.
3) TESTING.

A full test of the completed Shield Board requires assembly and integration of the Pill Reminder and all of its electronic components. The assembled Shield Board can be given a quick “smoke test” by inserting it into an Arduino Uno and then powering up the Uno. Use the multimeter on a voltage setting to check the voltage between the shield board Arduino power header pin “+5V” and “”GND”. The voltage should read close to 5.0 volts. The shield board is now ready to be assembled into the Pill reminder.

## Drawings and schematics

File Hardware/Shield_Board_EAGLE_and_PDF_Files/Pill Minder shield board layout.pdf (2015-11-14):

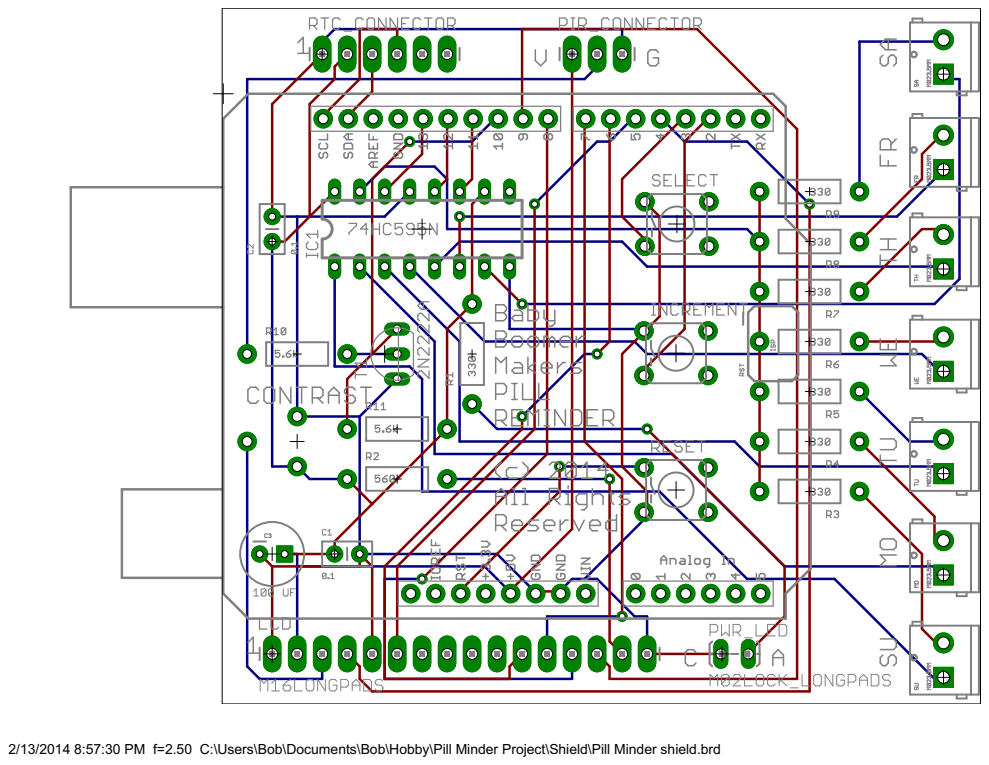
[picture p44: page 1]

2/13/2014 8:57:30 PM f=2.50 C:\Users\Bob\Documents\Bob\Hobby\Pill Minder Project\Shield\Pill Minder shield.brd

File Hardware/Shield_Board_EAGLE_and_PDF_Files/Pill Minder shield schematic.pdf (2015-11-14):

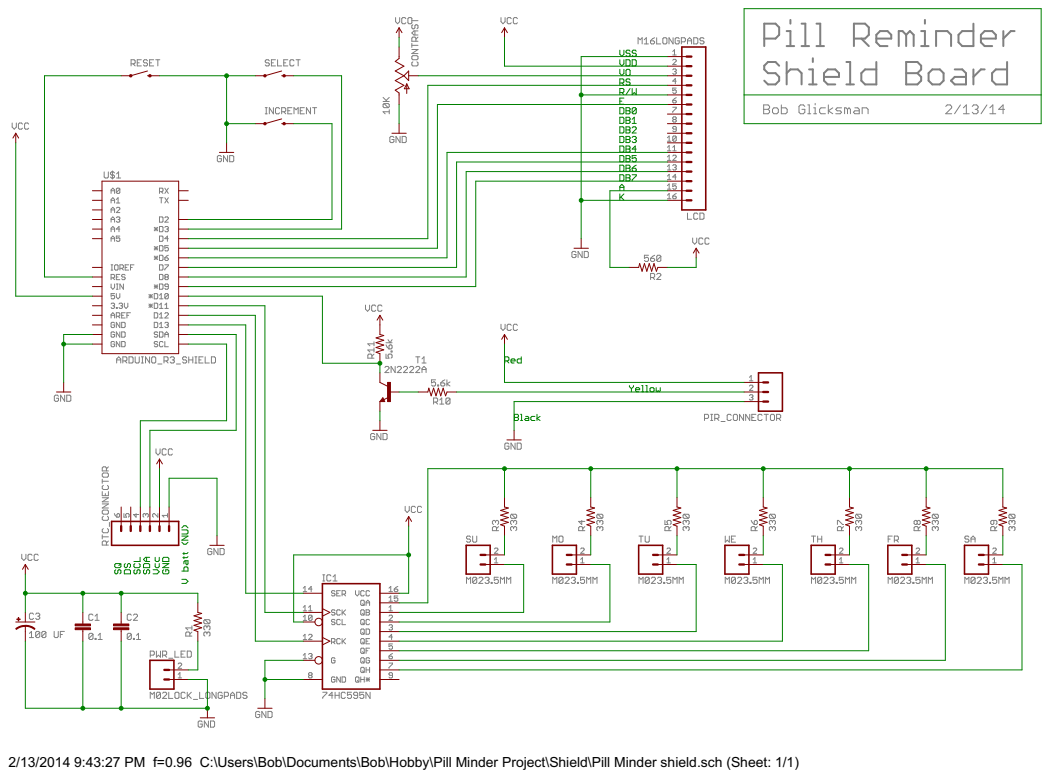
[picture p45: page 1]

2/13/2014 9:43:27 PM f=0.96 C:\Users\Bob\Documents\Bob\Hobby\Pill Minder Project\Shield\Pill Minder shield.sch (Sheet: 1/1)

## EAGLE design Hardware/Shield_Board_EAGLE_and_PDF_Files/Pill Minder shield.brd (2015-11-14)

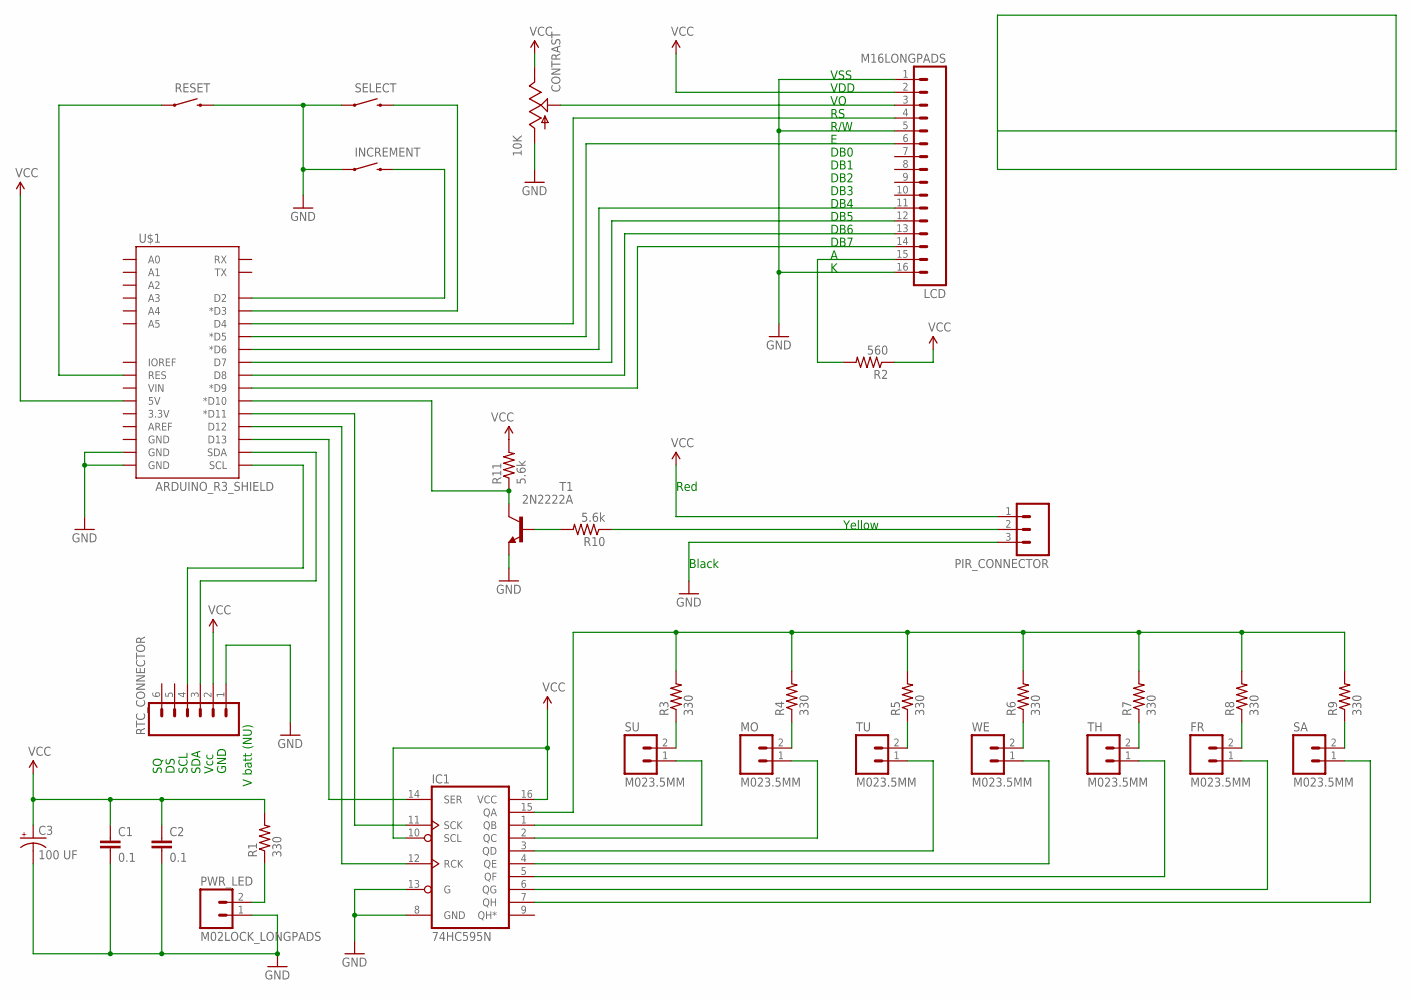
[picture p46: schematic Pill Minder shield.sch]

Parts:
C1, C2: 0.1; CAP-PTH-SMALL2
C3: 100 UF; CPOL-RADIAL-100UF-25V
CONTRAST: 10K; TRIM_POT
FR: M023.5MM; SCREWTERMINAL-3.5MM-2
IC1: 74HC595N; DIL16
INCREMENT: SWITCH-MOMENTARY-2PTH; TACTILE-PTH
LCD: M16LONGPADS; 1X16_LONGPADS
MO: M023.5MM; SCREWTERMINAL-3.5MM-2
PIR_CONNECTOR: M03LONGPADS; 1X03_LONGPADS
PWR_LED: M02LOCK_LONGPADS; 1X02_LOCK_LONGPADS
R1, R3, R4, R5, R6, R7, R8, R9: 330; AXIAL-0.4
R2: 560; AXIAL-0.4
R10, R11: 5.6k; AXIAL-0.4
RESET: SWITCH-MOMENTARY-2PTH; TACTILE-PTH
RTC_CONNECTOR: M06LONGPADS; 1X06_LONGPADS
SA: M023.5MM; SCREWTERMINAL-3.5MM-2
SELECT: SWITCH-MOMENTARY-2PTH; TACTILE-PTH
SU: M023.5MM; SCREWTERMINAL-3.5MM-2
T1: 2N2222A; TO92-EBC
TH: M023.5MM; SCREWTERMINAL-3.5MM-2
TU: M023.5MM; SCREWTERMINAL-3.5MM-2
U$1: ARDUINO_R3_SHIELD; UNO_R3_SHIELD
WE: M023.5MM; SCREWTERMINAL-3.5MM-2

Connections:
GND: C1.2, C2.2, C3.2 (-), CONTRAST.3 (A), IC1.8 (GND), IC1.13 (G), INCREMENT.1, LCD.1, LCD.5, LCD.16, PIR_CONNECTOR.3, PWR_LED.1, RESET.3 (2), RTC_CONNECTOR.1, SELECT.1, T1.E, U$1.GND@0 (GND), U$1.GND@1 (GND)
unnamed: RESET.1, U$1.RES
unnamed: IC1.7 (QH), SA.1
unnamed: IC1.1 (QB), SU.1
unnamed: R10.P$2 (2), T1.B
unnamed: IC1.2 (QC), MO.1
unnamed: IC1.3 (QD), TU.1
unnamed: IC1.4 (QE), WE.1
unnamed: IC1.5 (QF), TH.1
unnamed: FR.1, IC1.6 (QG)
unnamed: CONTRAST.1 (S), LCD.3
unnamed: SELECT.3 (2), U$1.D3 (*D3)
unnamed: INCREMENT.3 (2), U$1.D2
unnamed: IC1.14 (SER), U$1.D13
unnamed: IC1.12 (RCK), U$1.D12
unnamed: IC1.11 (SCK), U$1.D11 (*D11)
unnamed: RTC_CONNECTOR.4, U$1.SCL
unnamed: RTC_CONNECTOR.3, U$1.SDA
unnamed: LCD.4, U$1.D4
unnamed: LCD.6, U$1.D5 (*D5)
unnamed: LCD.11, U$1.D6 (*D6)
unnamed: LCD.12, U$1.D7
unnamed: LCD.13, U$1.D8
unnamed: LCD.14, U$1.D9 (*D9)
unnamed: LCD.15, R2.P$2 (2)
unnamed: R11.P$1 (1), T1.C, U$1.D10 (*D10)
unnamed: PWR_LED.2, R1.P$1 (1)
unnamed: PIR_CONNECTOR.2, R10.P$1 (1)
unnamed: R3.P$1 (1), SU.2
unnamed: MO.2, R4.P$1 (1)
unnamed: R5.P$1 (1), TU.2
unnamed: R6.P$1 (1), WE.2
unnamed: R7.P$1 (1), TH.2
unnamed: IC1.15 (QA), R3.P$2 (2), R4.P$2 (2), R5.P$2 (2), R6.P$2 (2), R7.P$2 (2), R8.P$2 (2), R9.P$2 (2)
unnamed: R9.P$1 (1), SA.2
unnamed: FR.2, R8.P$1 (1)
VCC: C1.1, C2.1, C3.1 (+), CONTRAST.2 (E), IC1.10 (SCL), IC1.16 (VCC), LCD.2, PIR_CONNECTOR.1, R1.P$2 (2), R2.P$1 (1), R11.P$2 (2), RTC_CONNECTOR.2, U$1.5V

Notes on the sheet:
V batt (NU)
GND
Vcc
SDA
SCL
VSS
VDD
R/W
DB0
DB1
DB2
DB3
DB4
DB5
DB6
DB7
Yellow
Black
Red

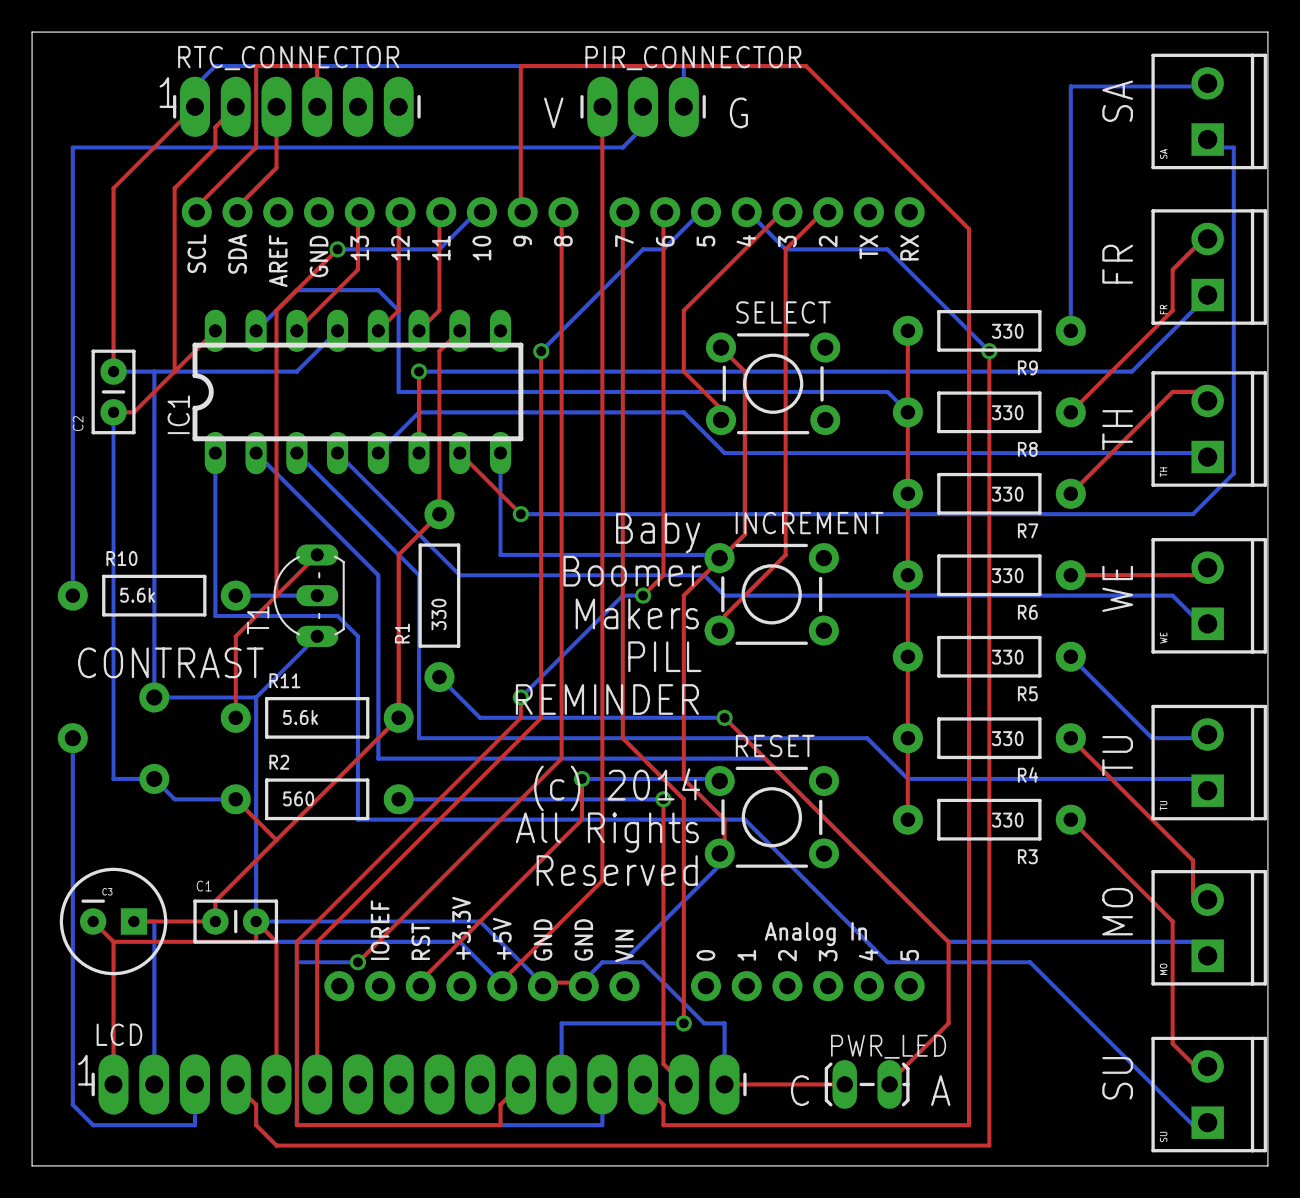
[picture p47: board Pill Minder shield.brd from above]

Board: 2 copper layers, 77.1 x 70.7 mm, 32 parts (0 on the bottom side), 37 nets.

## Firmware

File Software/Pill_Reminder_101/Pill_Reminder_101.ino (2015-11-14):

/*************************************** PILL REMINDER **************************************/
//
//    The PILL REMINDER helps a user to remember to take their pills at the correct times of the
//    day.  The device has two, 7-day sets of pill dispensers: one for morning (AM) medications
//    and one for evening (PM) medications.  There is an LED just above each pill dispenser.
//    If the current time is within a time wiondow for the user to take their AM or PM pills, 
//    the LED above the proper dispenser will light.  Otherwise, no LEDs light (helping the user to
//    avoid taking a missed dose too close to the next dose).  
//
//    The device does not sense if the user has actually opened the dispenser and removed the pills.  
//    Therefore, the proper LED lights throughout a "proper" pill taking time interval.  These
//    "proper pill taking time intervals" are specified in defined constants for LED on times and
//    LED off times for the AM pills and the PM pills. The constants and their defaults are:
//
//      - AM_ON_TIME: default is 6:00 AM
//      - AM_OFF_TIME: default is 1159 AM (noon)
//      - PM_ON_TIME: default is 6:00 PM
//      - PM_OFF_TIME: default is 11:59 PM (midnight)
//
//    These defined constants must be changed, and the program re-compiled and uploaded to the
//    device, if it is desired to change the AM and PM pill taking intervals.
//
//    Although the Pill Reminder does not sense the user opening a dispenser and removing the pills,
//    it is provided with an infrared proximity sensor (PIR) device.  Whenever the PIR is triggered
//    for the first time in any pill taking interval, the appropriate lit LED will blink for 
//    approximately 4 seconds, as an extra aide in gaining the user's attention.
//
//    A user with short term memory loss or mild dementia must be taught to open the dispenser
//    and take the pills therein only whenever an LED is lit, regardless of whether it is lit blinking
//    or solid.  If the dispenser under the lit LED is empty, the user has already taken the pill,
//    even if they do not remember doing so.  Caregivers must train users to only take pills in the
//    dispenser under the LED that is lit (if any) and not take any other pills, regardless of their
//    memory of pill taking.
//
//    The Pill Reminder contains a battery backed realtime clock module that maintains the date and time
//    even if the power is off.  The battery is rated to last at least 5 years.  If the battery is 
//    removed or fails, the user (or caregiver) is forced to manually set the current date and
//    time and the unit will not operate until this is done.  This feature prevents users from
//    taking pills at incorrect times due to a realtime click battery failure or other hardware problem.
//    
//    The device contains a 2 line, 16 character per line LCD that displays the current date, day of the
//    week and current time.  In addition, this display is used to promt a cargiver when setting the date
//    and the time.  The hardware and software automatically adjusts for daylight savings time (if so set)
//    and corrects for leap year; therefore, time setting should be a very infrequent function.
//
//    Normally, there are no controls for the user to operate (and therefore none for the user to mis-set).
//    Time setting requires opening the enclosure cover behind the display panel and depressing buttons
//    on the printed circuit board inside the unit, while following prompts on the LCD.  The time may only
//    be set when the device is first powered on or the "reset" button inside the unit is depressed.  Either
//    way that the device is reset, it starts off with a (nominally) 10 second period for the PIR to 
//    calibrate.  During this period, the LEDs will light in succession though approximately 4 cycles as a
//    self-test.  If, at any time during this calibration, the user presses the internal "select" button,
//    the LEDs will stop lighting and the unit will enter time setting mode.  In time setting mode, the user
//    advances through a menu using "select" and changes values for the displayed menu item using "increment".
//    Since time setting is an infrequent activity, only two buttons are provided and the user must step
//    through all menu items in order to set the device's internal time.  The button functions "wrap around"  
//    and the user may cycle through the prompts as many times as they wish, in order to check their settings.  
//    The device exits the time setting mode and re-enters the calibration mode only when the user presses
//    the increment button in response to the prompt to do so to set the date and time.  At this point
//    the device completes any PIR calibration time remaining and then enters the normal user mode.  In
//    the normal user mode, the device operates automatically with no user controls or setting capability.
//    It is necessary (intentionally) to reset the device in order to make any changes to the date and time.
//
//    Note:  if the LED on and off time defaults are to be changed by the users, please note that 
//    at least one minute (minimum interval supported by the code) is required between AM_OFF_TIME 
//    and PM_ON_TIME, and also between PM_OFF_TIME and AM_ON_TIME.  This minimum time, when all LEDs are off, 
//    is needed to reset the PIR blink state machine back to the disarmed state, so that the PIR functionality 
//    can then be re-armed for triggering.
//	
//  version 1.01 (initial public release)
//  author: Bob Glicksman
//  date: 3/12/14
//
//  IMPORTANT NOTICE:  
//    The Pill Reminder is released under a Creative Commons Attribution-ShareAlike Open Source license.  
//    Use of this software, device hardware, and documentation is subject to the terms and conditions of this license 
//    and by using the hardware, software and/or documentation in any manner, you are agreeing to abide by all terms
//    and conditions of the license.  To view a copy of this license, visit http://creativecommons.org/licenses/by-nc/4.0/
//    or send a letter to Creative Commons, 444 Castro Street, Suite 900, Mountain View, California, 94041, USA.
//    
//    The Pill Reminder is intended for hobbyist applications and for “do it yourself” assembly and use.  The user 
//    assumes all responsibility and liability for any damages, injuries or consequences resulting from the construction, 
//    implementation and use of this product or any part thereof. Complete terms and conditions of use can be found in the 
//    document "Terms_of_Use_License_and_Disclaimer" that is included in this release package.  This document can also
//    be found at http://www.shrimpware.com/pillreminder/TOU.html
//
//    Copyright © 2014 Shrimpware LLC. All rights reserved.


/****************************GLOBAL CONSTANTS AND VARIABLES ***********************************/

// INCLUDES (libraries)
#include <LiquidCrystal.h>      // library for LCD display
#include <Time.h>               // Arduino Time library
#include <Wire.h>               // Arduino I2C library
#include <DS1307RTC.h>          // Arduino library for DS1307 realtime clock
#include <Timezone.h>           // Arduino library for converting betweeen UTC and timezones, e.g. for DST
#include <EEPROM.h>             // Arduino library for writing to and reading from EEPROM

//  CONSTANTS

// debugging mode = advances time rapidly
// #define DEBUG    // comment this line out for normal operation

//    Patterns for lighting an LED
const byte LED_OFF = B00000000;
const byte SUN_AM =  B00000010;
const byte MON_AM =  B00000100;
const byte TUE_AM =  B00001000;
const byte WED_AM =  B00010000;
const byte THU_AM =  B00100000;
const byte FRI_AM =  B01000000;
const byte SAT_AM =  B10000000;

const byte SUN_PM =  B11111101;
const byte MON_PM =  B11111011;
const byte TUE_PM =  B11110111;
const byte WED_PM =  B11101111;
const byte THU_PM =  B11011111;
const byte FRI_PM =  B10111111;
const byte SAT_PM =  B01111111;

const unsigned long LED_TEST_DELAY = 150ul;    // time for LED to stay lighted in Calibrate self-test (150 ms)

//    PIR Calibration and self test time
const unsigned long PIR_CALIBRATE = 10000ul;  // 10 seconds (10,000 ms) per PIR spec sheet.

//    Time updating interval
const unsigned long TIME_UPDATE_INTERVAL = 250ul; // update the time display every 250 ms

//    Definition of Arduino pins used
//      Arduino pins used for LED shift register
const int latchPin = 12;
const int shiftPin = 11;
const int dataPin  = 13;

//      Arduino pins used for LCD display
const int RS     = 4;
const int ENABLE = 5;
const int D4     = 6;
const int D5     = 7;
const int D6     = 8;
const int D7     = 9;

//      Arduino pins used for push button switches
const int SELECT_PIN    = 3;
const int INCREMENT_PIN  = 2;

//      Arduino pin for PIR
const int pirPin    = 10;

//    Push button constants
const byte SELECT_ID = 0;         // SELECT is button number 0
const byte INCREMENT_ID = 1;      // INCREMENT is button number 1
const unsigned long DEBOUNCE_TIME = 20ul;  // 20 ms to debounce buttons.

//      LED lighting time periods (24 hour time for unambiguity)
const int AM_ON_TIME =   600;     // 6 am
const int AM_OFF_TIME =  1159;    // one minute before noon
const int PM_ON_TIME =   1800;    // 6 pm
const int PM_OFF_TIME =  2359;    // one minute before midnight 
const byte NUM_BLINKS = 16;    // blink selected LED for this number of quarter-seconds (16 = 4 seconds blink)

//      define states for PIR blink function
const byte PIR_DISARM    = 0x00;    // PIR blink function is disarmed - ignore PIR activity
const byte PIR_READY     = 0x01;    // PIR blink function is armed and ready to trigger LED blinking
const byte PIR_BLINKING  = 0x02;    // PIR has been triggered and is in the process of LED blinking
const byte PIR_COMPLETE  = 0x03;    // PIR blinking has completed and won't trigger again until next time cycle

//      Daylight savings time and timezone indications
const byte DST           = 0;      // Daylight savings time is to be observed and automated
const byte noDST         = 1;      //  Daylight savings time is not observed and only standard time is kept
const byte TZ_INDEX_MAX  = 1;      // Max - 1 number of entries in time zone possibilties -- currently 2 (DST, noDST)
const int TZ_ADDR        = 0;      // EEPROM address where user selected byte timeZoneIndex will be in non-volatile storage

//  GLOBAL VARIABLES

//    Arrays to index AM and PM LEDs
byte dayLightsAM[] = {SUN_AM, MON_AM, TUE_AM, WED_AM, THU_AM, FRI_AM, SAT_AM};
byte dayLightsPM[] = {SUN_PM, MON_PM, TUE_PM, WED_PM, THU_PM, FRI_PM, SAT_PM};

//    LCD display (lcd)
LiquidCrystal lcd(RS, ENABLE, D4, D5, D6, D7);

//    Rules for Daylight Savings Time using the Timezone library
TimeChangeRule dt = {"DT", Second, Sun, Mar, 2, 60};         // Daylight savings time is 60 minutes later than standard time
TimeChangeRule st = {"ST", First, Sun, Nov, 2, 0};           // Standard time, as set by the user
Timezone useDT(dt, st);                                      // Timezone object to use where daylight savings time is observed
Timezone useST(st, st);                                      // Timezone object to use where daylight savings time is not observed
     
//    The byte variable timeZoneIndex is used to determine if the user selected to observe daylight savings time
//    (timeZoneIndex = DST) or not to observe daylight savings time (timeZoneIndex = noDST).  Other values
//    may be added for regions of the world that observe different time zone change rules than the USA.
byte timeZoneIndex = DST;    // Default is to observe, and automate, daylight savings time conversions

//    Internal time
time_t currentTime;

/*********************END OF GLOBAL CONSTANTS AND VARIABLES ***********************************/
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

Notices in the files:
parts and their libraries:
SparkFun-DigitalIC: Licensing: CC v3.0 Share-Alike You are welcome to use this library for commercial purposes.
